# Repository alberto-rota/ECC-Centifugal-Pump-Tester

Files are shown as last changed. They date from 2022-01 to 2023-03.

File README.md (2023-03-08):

# ECC Centrifugal pump compliancy tester
An IR-based device for testing the compliance of ECC centrifugal pumps in terms of the hemolitic/thrombogenic effects of the magnetic impeller unstable rotations. 
Employs an LSTM classifier to distinguish proximity signals from compliant and non-compliant pumps.

_This project is in collaboration with Qura s.r.l._

***
* Active Contributors: **Alberto Rota**, Nicolò Pasini, Silvia Bonomi, Gaia Albani, Elisabetta Criseo
***

## Interface Installation
* Windows: *Link not yet Available* 
* Linux: *Link not yet Available*
You should contact the maintaining developer to have the links)

**NOTE:** The interface embeds the ML kodel for the compliancy classification, hence at the moment it includes the whole TensorFlow framework. The size of the download is close to 1GB, but will be optimized in the future

**Requirements:** No requirement is necessary. The program runs as a standalone application.

After downloading, copy the folder in the directory of your choice. To run the interface excecute the file `qura_pump_tester`, which opens the following window

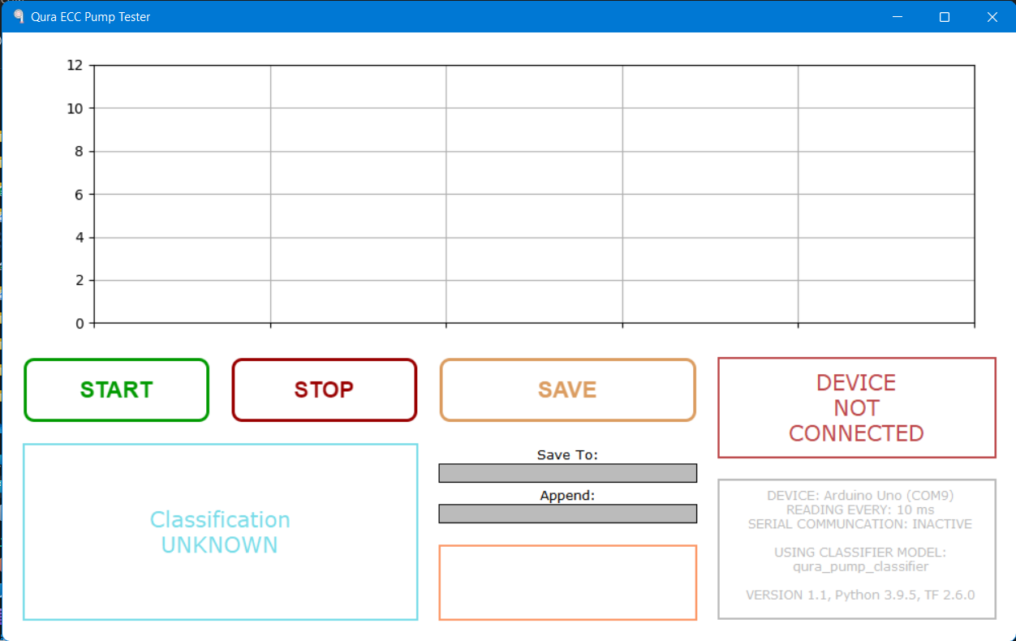
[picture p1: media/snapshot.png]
snap


***
## How to use this Interface
After being plugged in, the device should be detected automatically in the top-right frame, which becomes green and displays the device name, COM-Port and Baudrate. If the Serial Communication is not initialized correctly, the bottom-right gray frame shows `SERIAL COMMUNICATION: INACTIVE`: check that the device name in the `config` file is correct.
With serial communication estabilished, the workflow to be followed is:
* Press the green **START** button to start recording the signals. Ideally, the **START** button should be pressed when the pump is steadily rotating at 500 rpm. The recordings will be displayed in the cart area in real time
* Press the red **STOP** button to stop the recording. Ideally, the **STOP** button should be pressed when the pump is still rotating at 500 rpm and before stopping the driver motion. After this button is pressed, the AI model performs the classification and displays the output in the bottom-left frame
* Press the orange **SAVE** button to save the recording for the last pump tested on a *.csv* file. The file will be saved in the folder specified in the "Save to:" textbox; if any text is specified in the "Append:" textbox, that same text will be appended to the filename. For example, with:
  - *Save to:* C:\Users\qura\tests
  - *Append:* appended

The file will be saved as:
`C:\Users\qura\tests\DDMMYY_HHMMSS_appended.csv` [DayMonthYear_HourMinutesSeconds]

***

## Project Overview
The device is placed on top of the pump while it is mounted and rotating on the driver. The entity of the fluttering is measured as the distance from the 6 IR phototransistors (OPB730F) placed on the pump roof facing downward. The bell-shaped sensitivity curve of the OPB730F ([see datasheet](https://github.com/alberto-rota/Qura-ECC-Centifugal-Pump-Tester/tree/main/media/OPB730F%20Datasheet.pdf)) suggest an inverse relationship between distance and output voltage. The signals are then aquired by an ESP32 and sent to a computer in serial communication

The acquisition circuit is reported below:

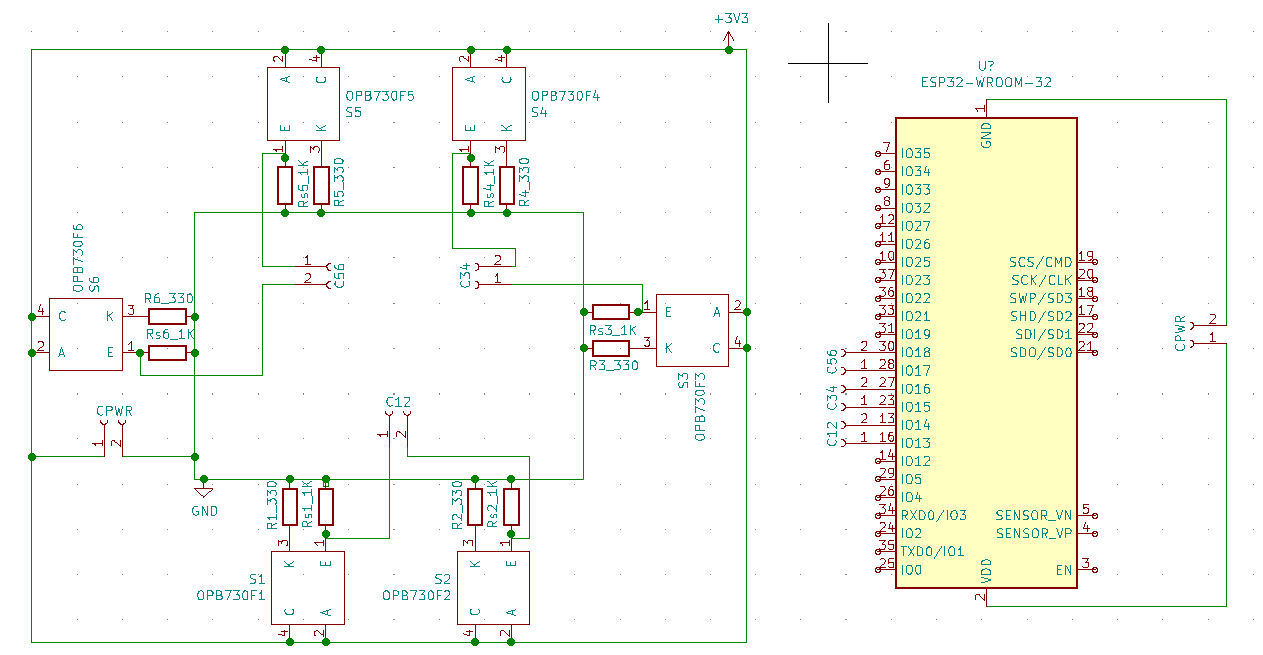
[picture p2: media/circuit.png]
circuit


and it has been embedded in a custom-made PCB, which connects to the ESP32 via JST connectors.
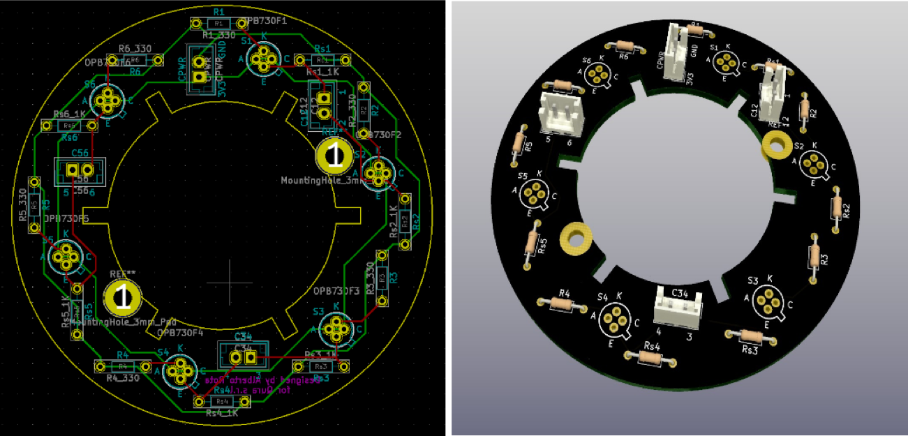
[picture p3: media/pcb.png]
pcb


## Compliancy assessment
Since no evitent distinction critheria emerge from the acquired signals, an AI-based classifier has been trained by recording the signals from 51 pumps at low (100 rpm) and high (500 rpm) speed.
The model is based on a LSTM architecture. The signal is divided in 75-samples-long windows, sliced from the signals (which may have different length) with a padding of 25. No data-augmentation is performed. After an 8-fold cross validation, the model from the best fold classified a test set with an **accuracy of 88%**. 

*The LSTM model is being developed further, no additonal details on the results are therefore provided*

## Prototype Design 
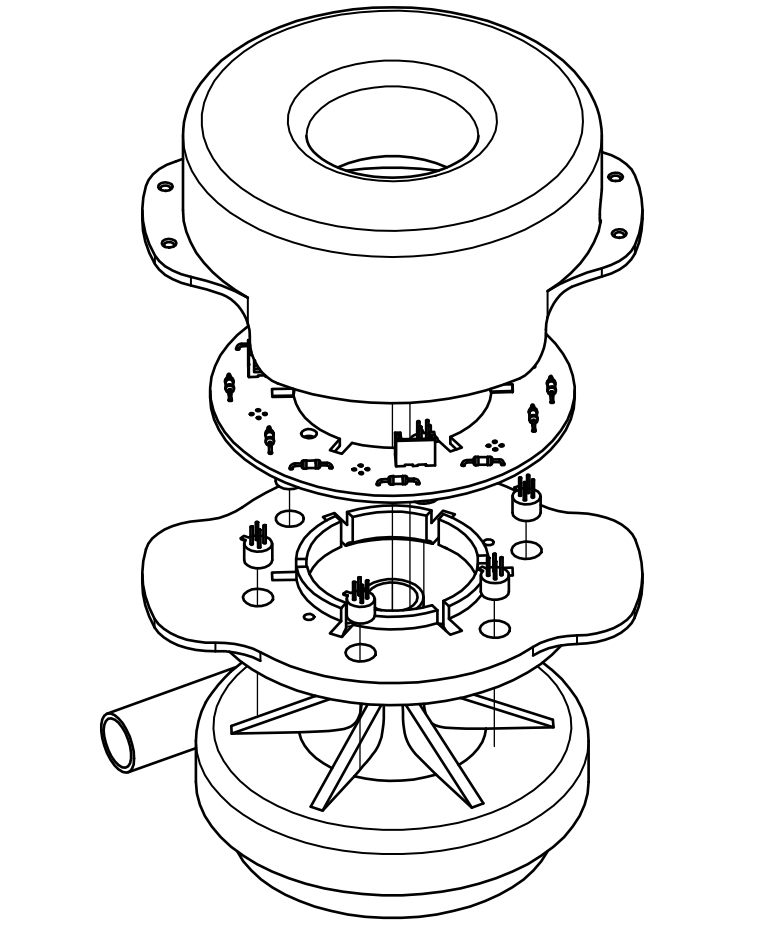
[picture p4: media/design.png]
design


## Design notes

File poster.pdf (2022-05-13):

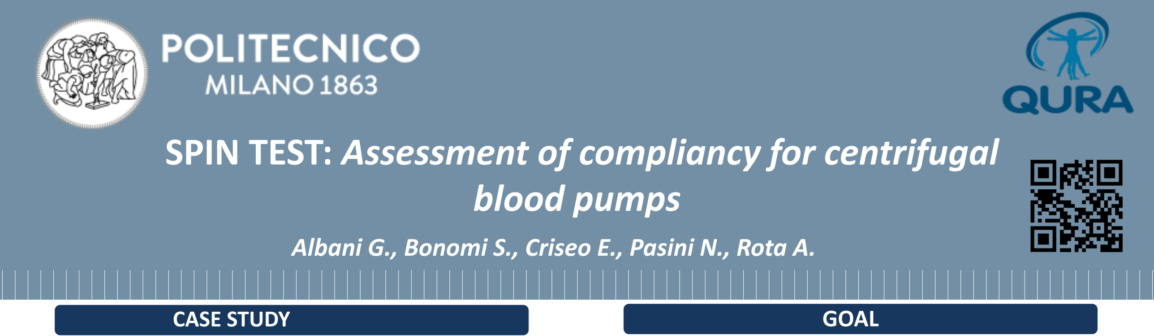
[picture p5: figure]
blood pumps; CASE STUDY; GOAL

# SPIN TEST: Assessment of compliancy for centrifugal

Centrifugal Blood Pumps: devices used during extracorporeal circulation; the blood flow enters from the inlet of the pump and is pushed by the rotor in such a way as to exit through the outlet, oriented at an angle of 90 ° to the inlet

Company
operator

Hearing the
noise produced
by the pump

Motion of
pump’s
impeller

Classify the pumps
in compliant and
not compliant

Find a STANDARDIZED, AUTOMATED and NON-DAMAGING protocol to test the pump in order to assess its acceptability

1. Optimize the process
2. Standardize the modality to eliminate the intra-subject variability
3. Not distructive test
4. Reproducible
5. Not invasive approach

## MATHERIALS AND METHODS

## RESULTS AND DISCUSSION

Efficacy: measure how much the impeller approaches or moves away from the sensors

OPB730F sensors

✓Linearity range [2.5-10mm] ✓Filter
✓Internal barrier
✓Max Input diode’s current = 50 mA ✓R diode > 36Ω

Infrared
LED | Transistor

MODEL IDEA

1, S≥0.5 ⇒ Compliant
0, S<0.5 ⇒ Non Compliant

C=

K=2⋅|S−0.5|⋅100

The classifier works applying a simply threshold:

The confidence of the classificator is given by:

Initial dataset is composed by 33 pumps:
- 11 pumps are used to calculate the the accuracy of the model
- 22 pumps are used for the training phase

Problem: movement of the impeller which tends to make a flickering movement along the z-x and z-y plane. This could cause haemolysis and thrombi

z

Solution: Spin Test to quantify the flickering of the impeller and classify the pumps between compliant and non-compliant

Today’s
approach

THE DATASET

Test on-site at Qura s.r.l. to validate our model: 13 pumps tested not included in the training dataset

Initial Results
29 pumps | Properly classified
4 pumps | False negative
Accuracy | 0.88

Results
11 pumps | Properly classified
2 pumps | False negative
Accuracy | 0.84

### VALIDATION TEST

The results
confirm the
validity of the
model

Explanation: when a voltage is applied, the diode emits IR light that propagates until hits an object and it is reflected towards the sensor

Every sensor used
is associated to a
circuit

PCB (Printed Circuit Board): 6 sensors were used to achieve a precise measure of the impeller fluttering.
The PCB reduces the extension of the circuits and makes the set-up compact. The PCB is then fixed to the pump through a support which allows maintaining the sensors in the right position

Development Board: the development board is what brings the output signals of the sensors as input for the graphical interface. In this way the signals are displayed to the operator in a clear way

Data Acquisition: the set-up with is used to register the signal from 51 pumps. These were divided a priori between compliant and non compliant.

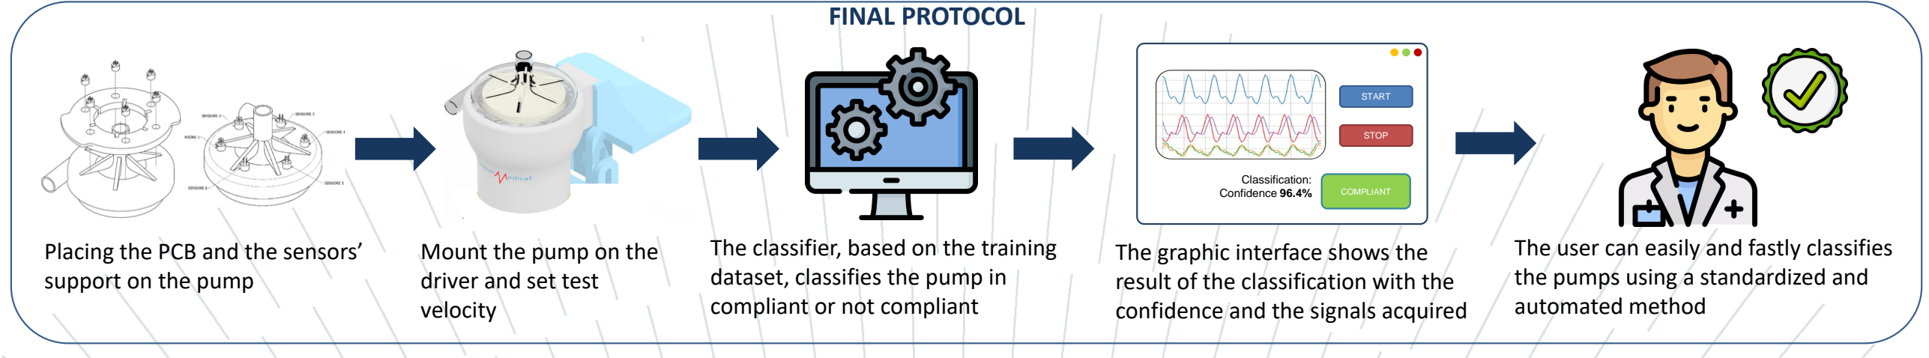
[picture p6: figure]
START; STOP; COMPLIANT; Classification: Confidence 96.4%; FINAL PROTOCOL; Placing the PCB and the sensors’ support on the pump; Mount the pump on the driver and set test velocity; The classifier, based on the training dataset, classifies the pump in compliant or not compliant; The graphic interface shows the result of the classification with the confidence and the signals acquired; the pumps using a standardized and automated method

The user can easily and fastly classifies

Impact: this would mean increasing the efficiency of the the process in terms of time and human resources

New approach:

OPTICAL PROXIMITY SENSORS | PCB AND DEVELOPMENT BOARD | MACHINE LEARNING

the operator no longer has a determining role in the classification of the pumps. In fact, through a machine learning model, the classification becomes more objective

CNN Model Implementation

1. The raw data obtained from the sensors is elaborated using data augmentation, in this way it is obtained the training set
2. Preparation of test-set
3. Definition of model architecture

Model Tuning: defining optimal parameters to get the best result with the model architecture chosen. The parameters to be optimized are: dimension of the windows used to elaborate the data, filters’ dimension and their number

Data acquisition was performed using two kinds of test: imposing a rotation of 100 rpm or 500 rpm, both times for 5 seconds

Albani G., Bonomi S., Criseo E., Pasini N., Rota A.

Classification

Expected Result

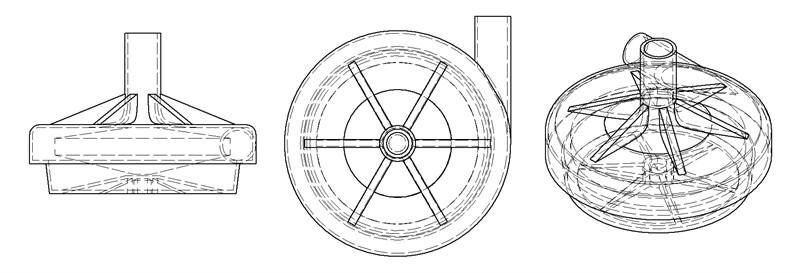
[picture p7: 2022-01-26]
media/eccpump.png

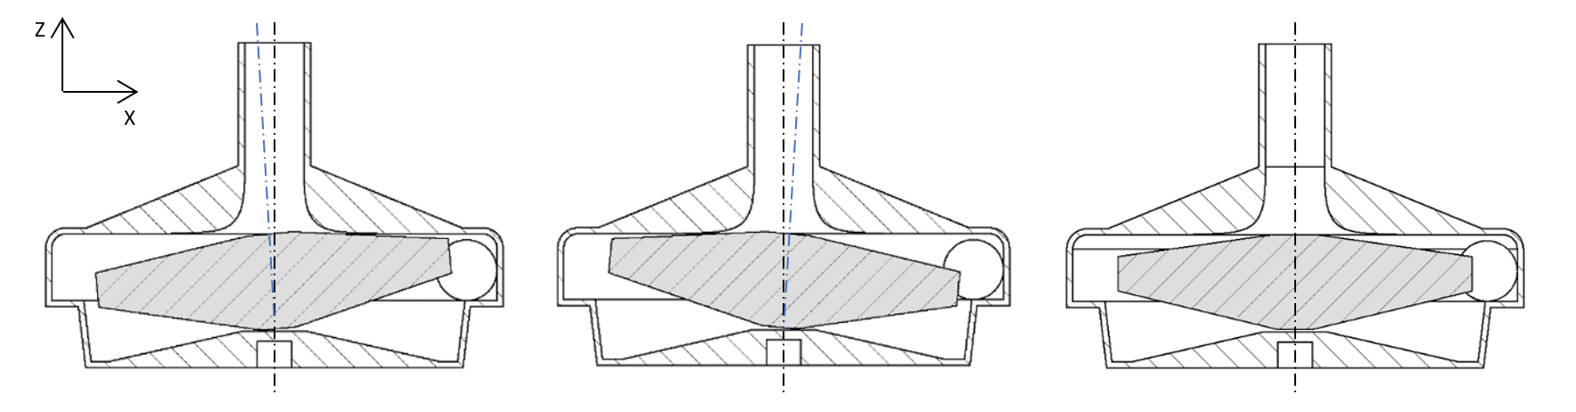
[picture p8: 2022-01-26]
media/fluttering.png

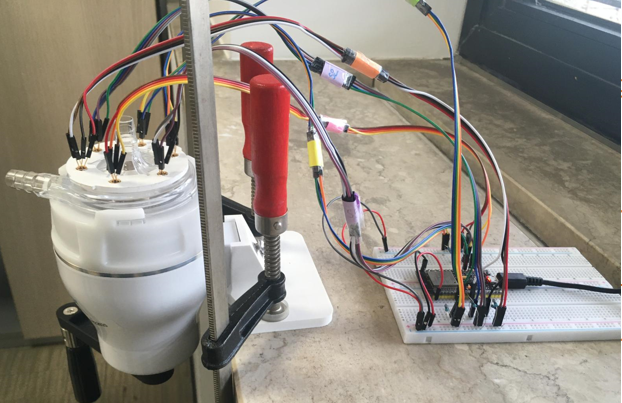
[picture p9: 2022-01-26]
media/prototype.png

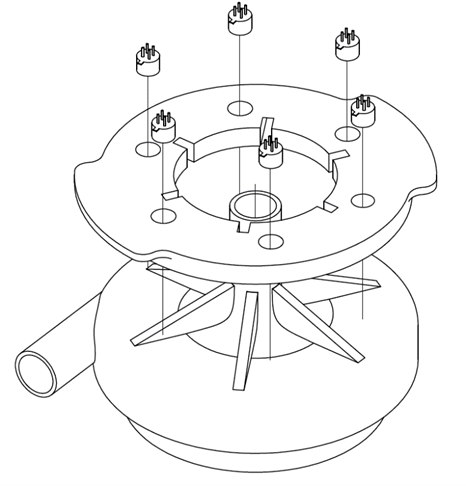
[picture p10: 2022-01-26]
media/sensorpositioning.png

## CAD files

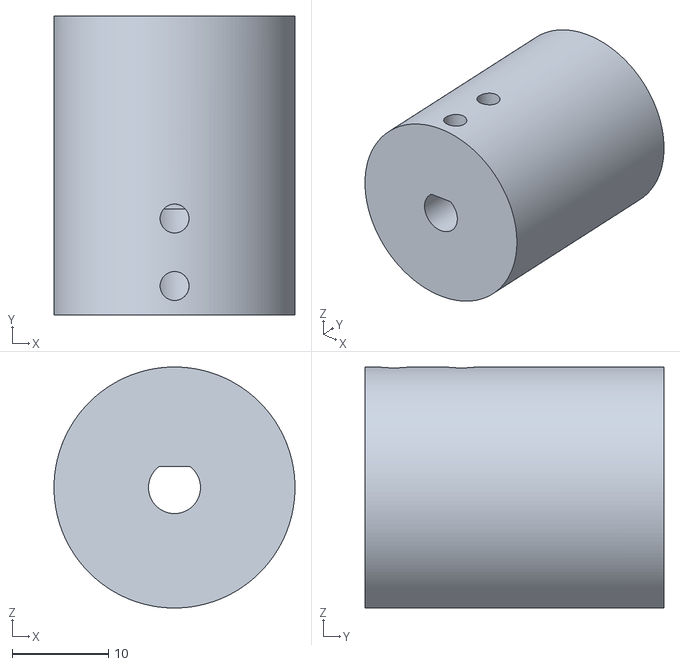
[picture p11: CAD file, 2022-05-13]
design/MotorDriverCoupler.stl
25.0 x 31.0 x 25.0

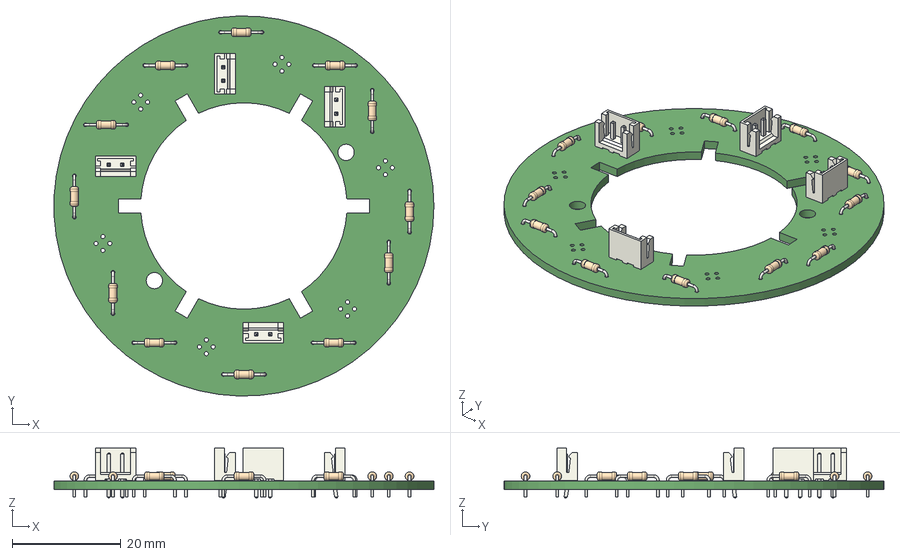
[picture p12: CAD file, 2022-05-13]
pcb/qura_pump_pcb_model.step
70.0 x 70.0 x 9.20 mm

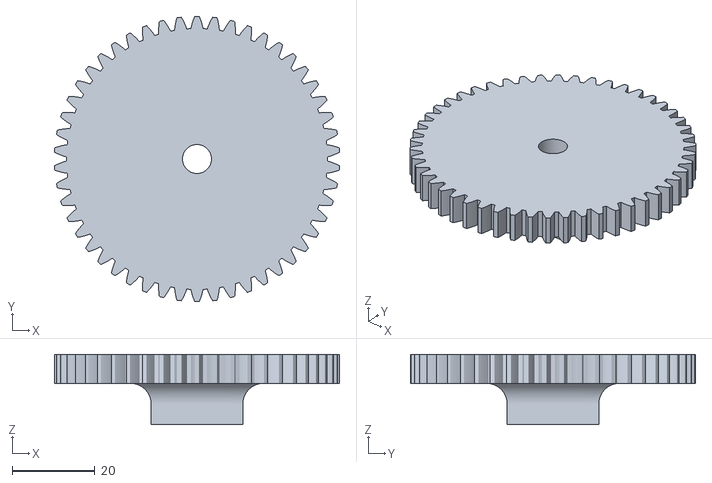
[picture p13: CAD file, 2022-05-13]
design/BigGear.stl
68.9 x 69.0 x 17.0

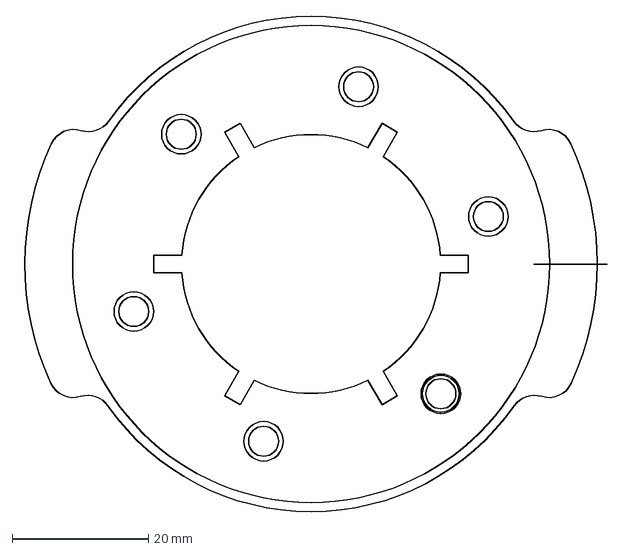
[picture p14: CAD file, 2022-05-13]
pcb/pcb_footprint.dxf
86.7 x 72.7 mm

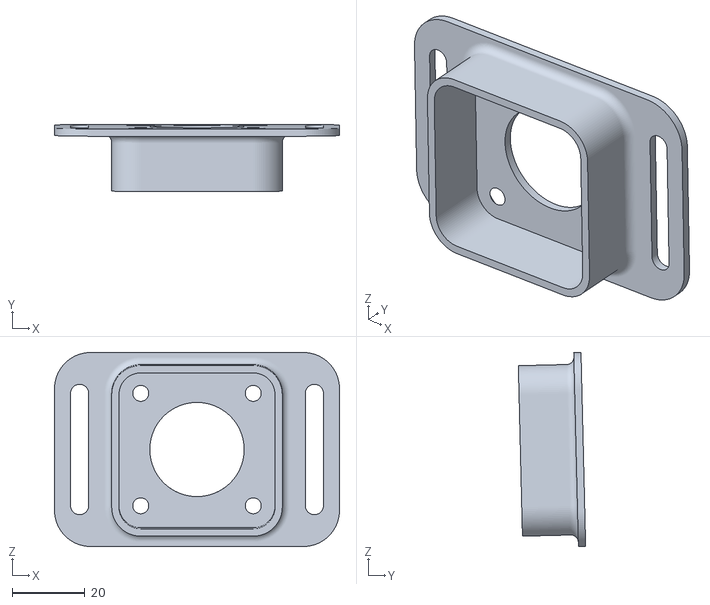
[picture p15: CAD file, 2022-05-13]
design/Slider.stl
78.5 x 18.6 x 53.5

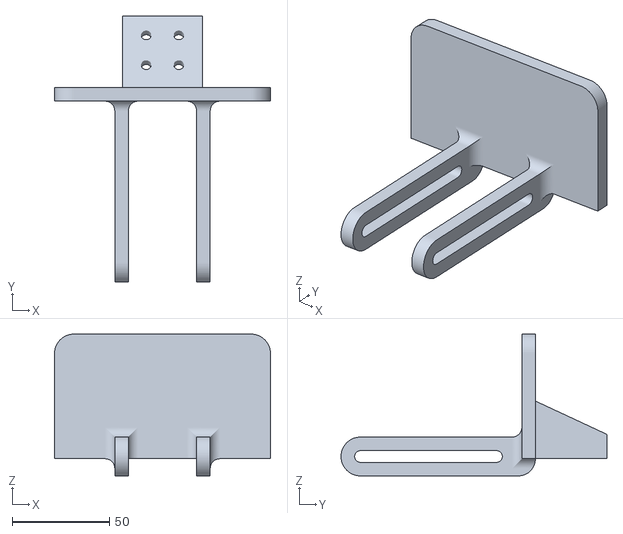
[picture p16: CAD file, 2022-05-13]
design/driver_lock.stl
111.1 x 136.8 x 73.0

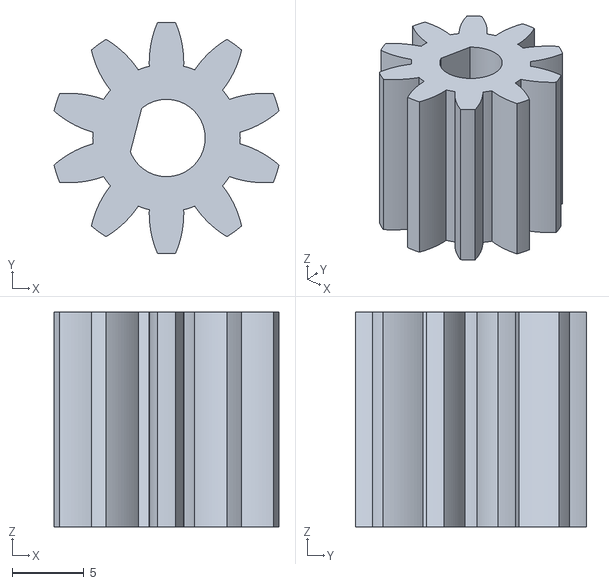
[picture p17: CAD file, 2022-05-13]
design/SmallGear.stl
15.7 x 16.2 x 15.0

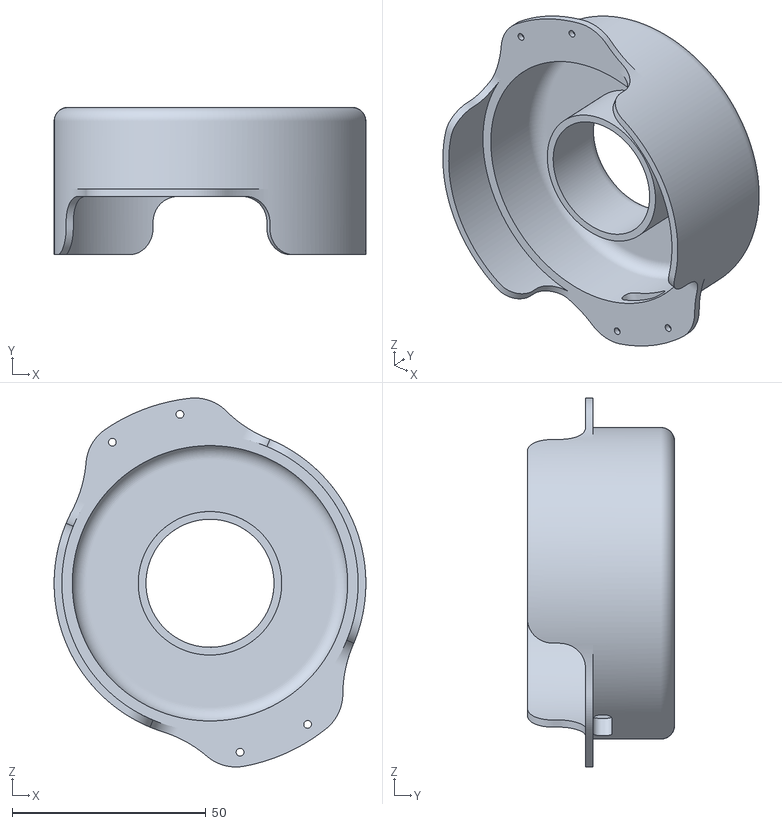
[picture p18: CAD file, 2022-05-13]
design/Case.stl
80.4 x 38.0 x 95.2

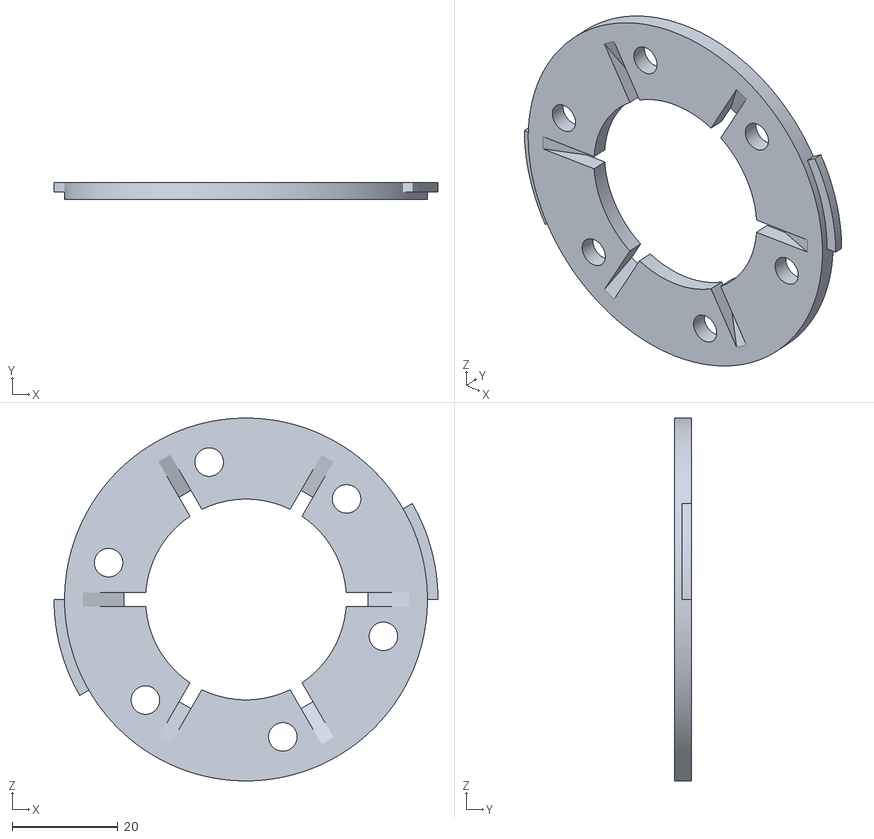
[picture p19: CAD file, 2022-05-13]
design/sensor_housing_v3.stl
72.7 x 3.20 x 68.7

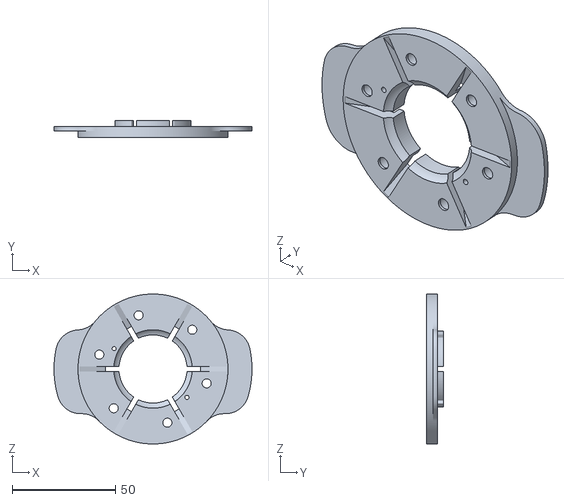
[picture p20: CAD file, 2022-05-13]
design/Housing.stl
96.0 x 8.20 x 72.7

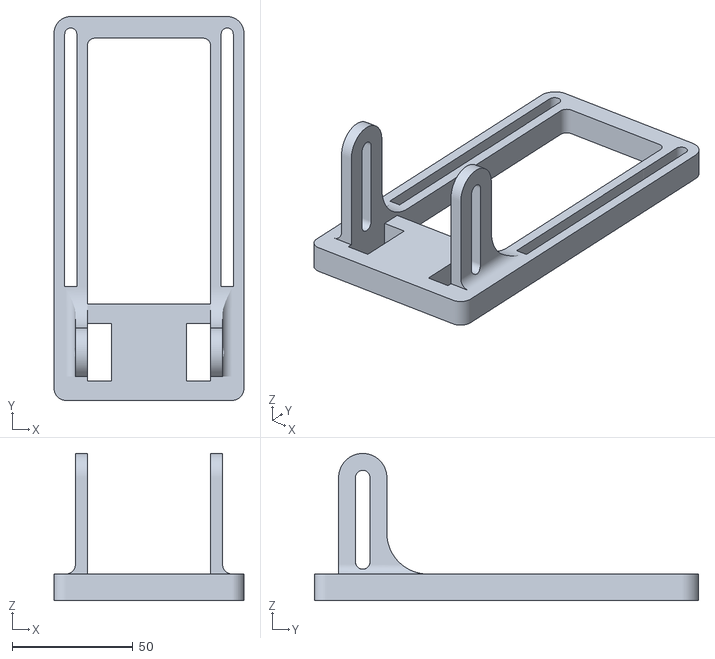
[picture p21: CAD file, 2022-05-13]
design/VSlider.stl
78.7 x 159.2 x 61.0

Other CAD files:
design/Assembly-1.dwg
design/Pump_drawing.dwg
design/OldVersions/Pump_drawing.0001.dwg
design/Assembly.iam
design/Assembly/Design Accelerator/Spur Gear11.ipt
design/Assembly/Design Accelerator/Spur Gear12.ipt
design/Assembly/Design Accelerator/Spur Gear13.ipt
design/Assembly/Design Accelerator/Spur Gear21.ipt
design/Assembly/Design Accelerator/Spur Gear22.ipt
design/Assembly/Design Accelerator/Spur Gears1.iam
design/Assembly/Design Accelerator/Spur Gears2.iam
design/Assembly1.iam
design/Case.ipt
design/Driver.ipt
design/DriverMount.iam
design/Driver_lock.ipt
design/Frame.ipt
design/Housing.ipt
design/Impeller.ipt
design/Motor-Driver Coupler.ipt
design/OldVersions/Assembly.0049.iam
design/OldVersions/Case.0003.ipt
design/OldVersions/Complete.0004.iam
design/OldVersions/Driver.0008.ipt
design/OldVersions/DriverMount.0004.iam
design/OldVersions/Driver_lock.0015.ipt
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

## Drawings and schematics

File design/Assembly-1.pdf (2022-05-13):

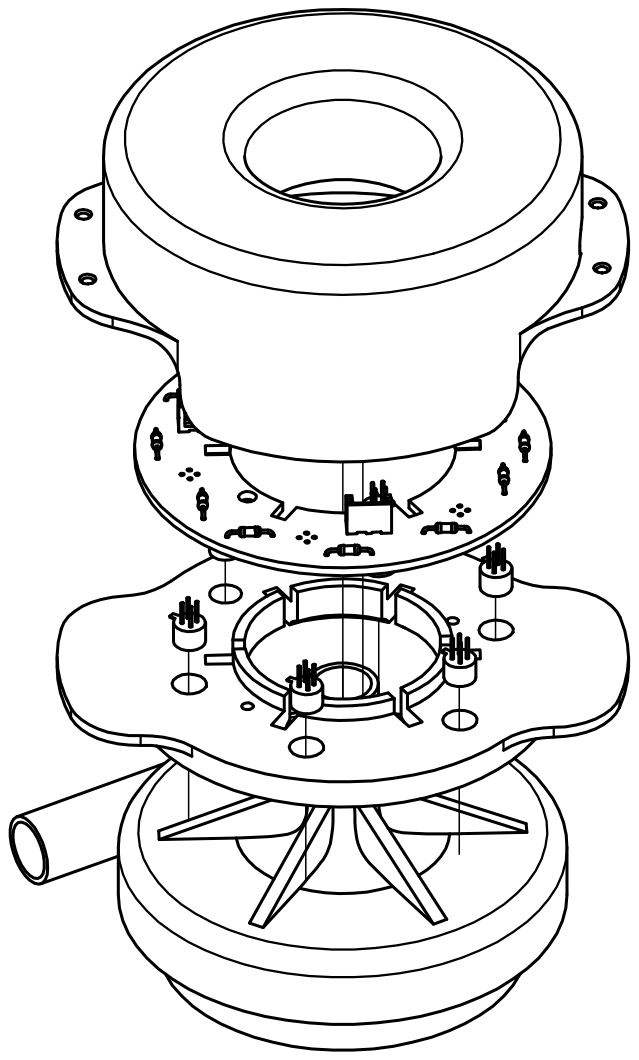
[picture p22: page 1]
Designed by; Checked by; Approved by; Date

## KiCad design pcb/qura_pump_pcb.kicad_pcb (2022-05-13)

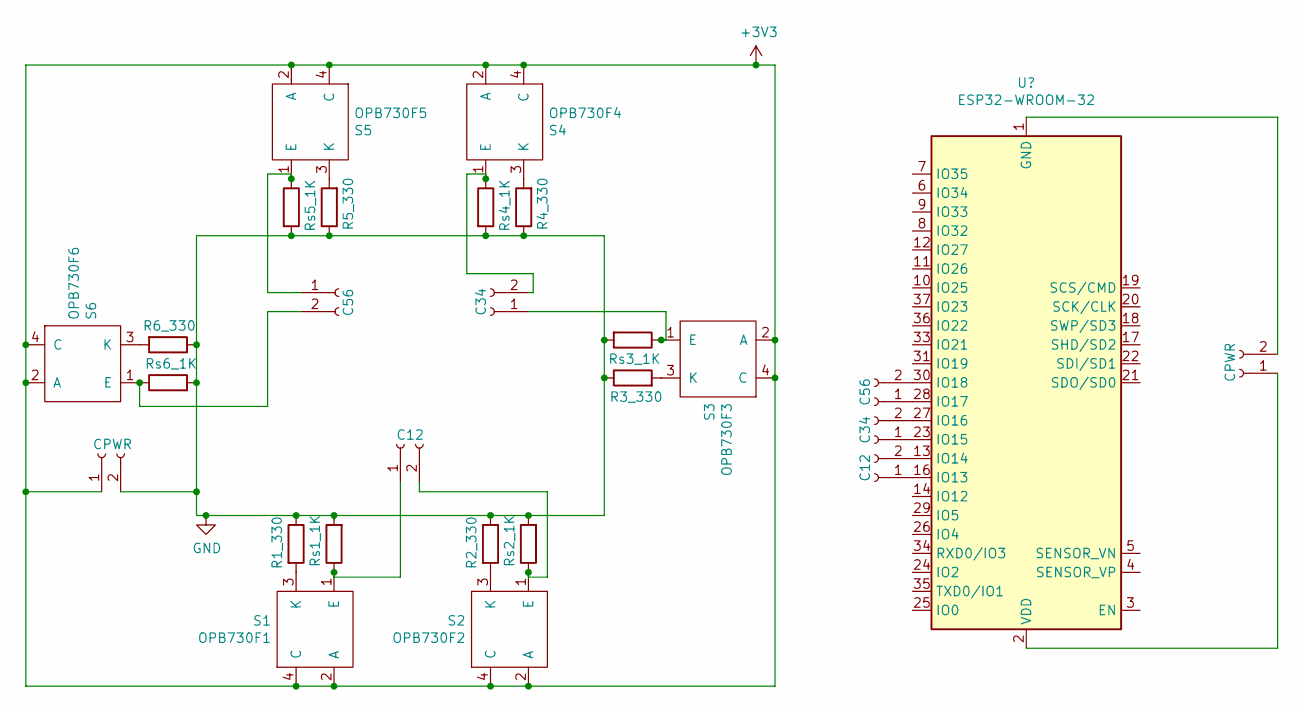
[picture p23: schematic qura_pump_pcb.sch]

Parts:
C12: C12; JST_EH_B2B-EH-A_1x02_P2.50mm_Vertical
C34: C34; JST_EH_B2B-EH-A_1x02_P2.50mm_Vertical
C56: C56; JST_EH_B2B-EH-A_1x02_P2.50mm_Vertical
CPWR1: CPWR; JST_EH_B2B-EH-A_1x02_P2.50mm_Vertical
OPB730F1: S1; OPB730F
OPB730F2: S2; OPB730F
OPB730F3: S3; OPB730F
OPB730F4: S4; OPB730F
OPB730F5: S5; OPB730F
OPB730F6: S6; OPB730F
R1: R1_330; R_Axial_DIN0204_L3.6mm_D1.6mm_P7.62mm_Horizontal
R2: R2_330; R_Axial_DIN0204_L3.6mm_D1.6mm_P7.62mm_Horizontal
R3: R3_330; R_Axial_DIN0204_L3.6mm_D1.6mm_P7.62mm_Horizontal
R4: R4_330; R_Axial_DIN0204_L3.6mm_D1.6mm_P7.62mm_Horizontal
R5: R5_330; R_Axial_DIN0204_L3.6mm_D1.6mm_P7.62mm_Horizontal
R6: R6_330; R_Axial_DIN0204_L3.6mm_D1.6mm_P7.62mm_Horizontal
Rs1: Rs1_1K; R_Axial_DIN0204_L3.6mm_D1.6mm_P7.62mm_Horizontal
Rs2: Rs2_1K; R_Axial_DIN0204_L3.6mm_D1.6mm_P7.62mm_Horizontal
Rs3: Rs3_1K; R_Axial_DIN0204_L3.6mm_D1.6mm_P7.62mm_Horizontal
Rs4: Rs4_1K; R_Axial_DIN0204_L3.6mm_D1.6mm_P7.62mm_Horizontal
Rs5: Rs5_1K; R_Axial_DIN0204_L3.6mm_D1.6mm_P7.62mm_Horizontal
Rs6: Rs6_1K; R_Axial_DIN0204_L3.6mm_D1.6mm_P7.62mm_Horizontal

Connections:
+3V3: CPWR1.1, OPB730F1.2 (A), OPB730F1.4 (C), OPB730F2.2 (A), OPB730F2.4 (C), OPB730F3.2 (A), OPB730F3.4 (C), OPB730F4.2 (A), OPB730F4.4 (C), OPB730F5.2 (A), OPB730F5.4 (C), OPB730F6.2 (A), OPB730F6.4 (C); also elsewhere on the board
GND: CPWR1.2, R1.1, R2.1, R3.1, R4.1, R5.1, R6.1, Rs1.2, Rs2.2, Rs3.2, Rs4.2, Rs5.2, Rs6.2; also elsewhere on the board
unnamed: C12.1, OPB730F1.1 (E), Rs1.1
unnamed: C12.2, OPB730F2.1 (E), Rs2.1
unnamed: C34.1, OPB730F3.1 (E), Rs3.1
unnamed: C34.2, OPB730F4.1 (E), Rs4.1
unnamed: C56.1, OPB730F5.1 (E), Rs5.1
unnamed: C56.2, OPB730F6.1 (E), Rs6.1
unnamed: OPB730F1.3 (K), R1.2
unnamed: OPB730F2.3 (K), R2.2
unnamed: OPB730F3.3 (K), R3.2
unnamed: OPB730F4.3 (K), R4.2
unnamed: OPB730F5.3 (K), R5.2
unnamed: OPB730F6.3 (K), R6.2

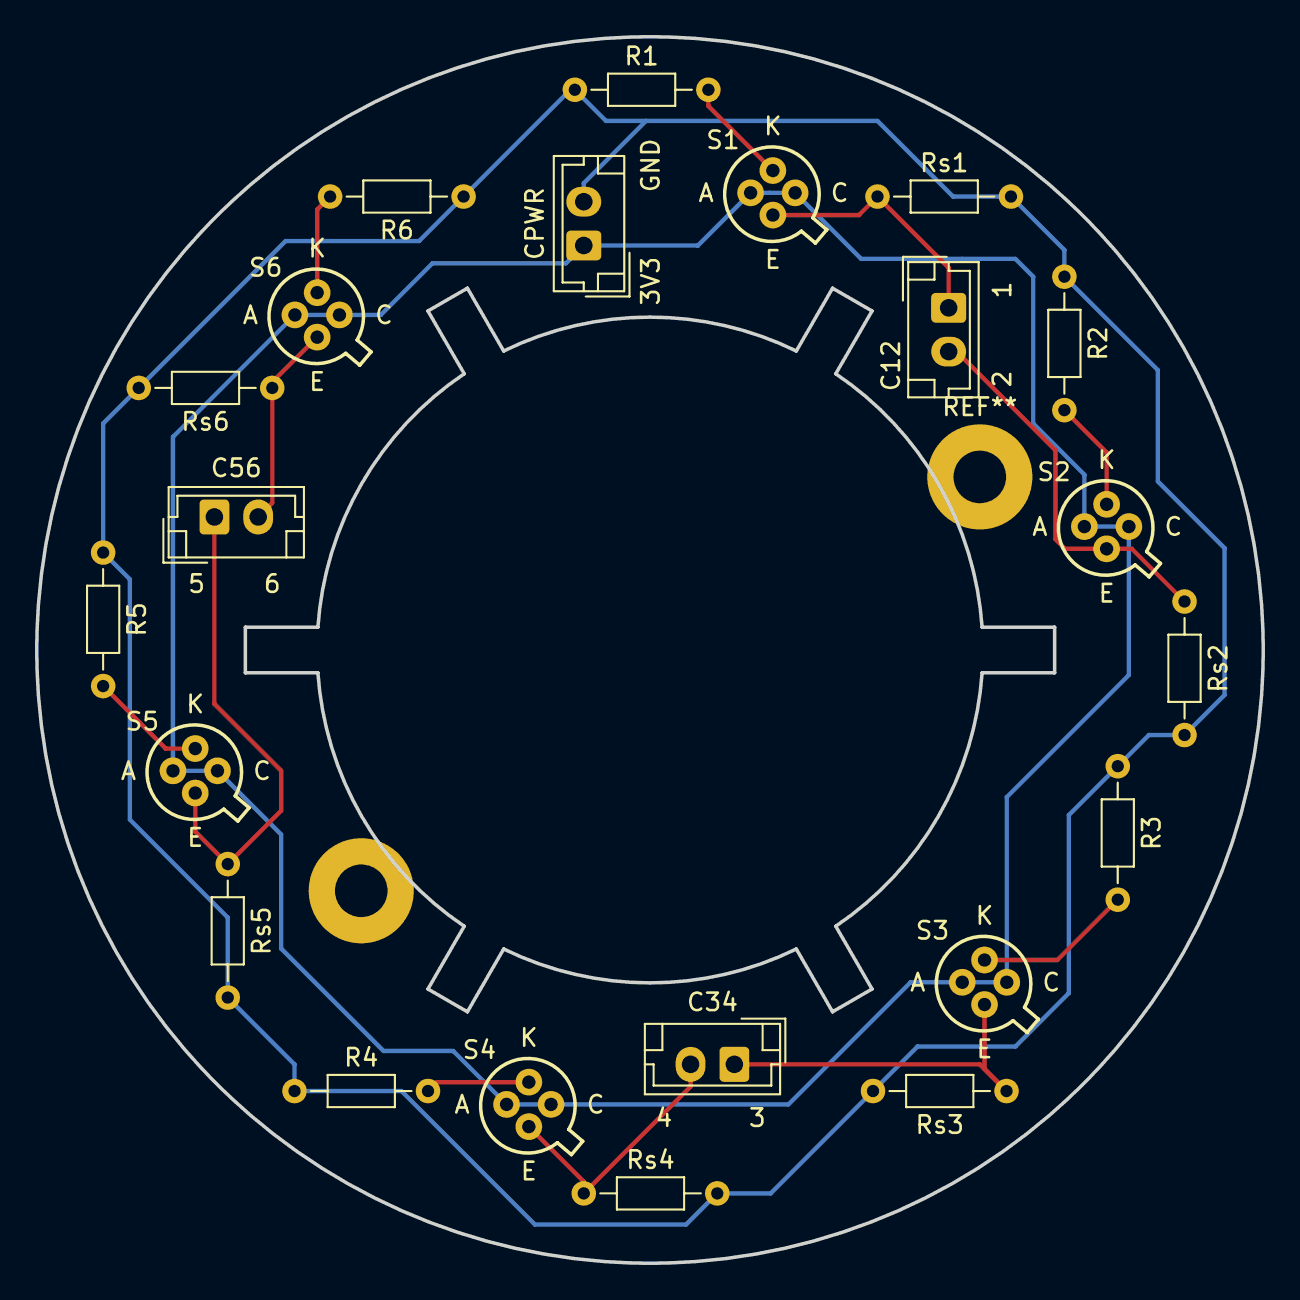
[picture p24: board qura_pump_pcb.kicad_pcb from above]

Board: 2 copper layers, 70.0 x 70.0 mm, 22 parts (0 on the bottom side), 14 nets.

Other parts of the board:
CPWR: CPWR; JST_EH_B2B-EH-A_1x02_P2.50mm_Vertical

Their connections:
+3V3: CPWR.1; also elsewhere on the board
GND: CPWR.2; also elsewhere on the board

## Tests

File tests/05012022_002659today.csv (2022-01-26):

8.699999999999999956e-01 | 3.259999999999999787e+00 | 5.509999999999999787e+00 | 7.889999999999999680e+00 | 9.759999999999999787e+00 | 1.000000000000000000e+01
8.399999999999999689e-01 | 3.330000000000000071e+00 | 5.620000000000000107e+00 | 7.980000000000000426e+00 | 9.310000000000000497e+00 | 1.053999999999999915e+01
8.000000000000000444e-01 | 3.390000000000000124e+00 | 5.719999999999999751e+00 | 8.000000000000000000e+00 | 8.789999999999999147e+00 | 1.155000000000000071e+01
7.700000000000000178e-01 | 3.450000000000000178e+00 | 5.799999999999999822e+00 | 7.940000000000000391e+00 | 8.320000000000000284e+00 | 1.200000000000000000e+01
7.399999999999999911e-01 | 3.509999999999999787e+00 | 5.870000000000000107e+00 | 7.830000000000000071e+00 | 8.039999999999999147e+00 | 1.141000000000000014e+01
7.099999999999999645e-01 | 3.560000000000000053e+00 | 5.929999999999999716e+00 | 7.650000000000000355e+00 | 8.029999999999999361e+00 | 1.038000000000000078e+01
6.700000000000000400e-01 | 3.620000000000000107e+00 | 5.969999999999999751e+00 | 7.429999999999999716e+00 | 8.279999999999999361e+00 | 1.000999999999999979e+01
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

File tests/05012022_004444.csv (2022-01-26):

1.860000000000000098e+00 | 3.870000000000000107e+00 | 4.139999999999999680e+00 | 7.870000000000000107e+00 | 8.089999999999999858e+00 | 1.165000000000000036e+01
1.879999999999999893e+00 | 3.839999999999999858e+00 | 4.080000000000000071e+00 | 7.700000000000000178e+00 | 8.000000000000000000e+00 | 1.065000000000000036e+01
1.889999999999999902e+00 | 3.799999999999999822e+00 | 4.040000000000000036e+00 | 7.490000000000000213e+00 | 8.199999999999999289e+00 | 1.000999999999999979e+01
1.909999999999999920e+00 | 3.759999999999999787e+00 | 4.009999999999999787e+00 | 7.250000000000000000e+00 | 8.609999999999999432e+00 | 1.040000000000000036e+01
1.919999999999999929e+00 | 3.709999999999999964e+00 | 4.000000000000000000e+00 | 6.980000000000000426e+00 | 9.130000000000000782e+00 | 1.140000000000000036e+01
1.939999999999999947e+00 | 3.660000000000000142e+00 | 4.009999999999999787e+00 | 6.719999999999999751e+00 | 9.609999999999999432e+00 | 1.199000000000000021e+01
1.949999999999999956e+00 | 3.609999999999999876e+00 | 4.030000000000000249e+00 | 6.480000000000000426e+00 | 9.929999999999999716e+00 | 1.155000000000000071e+01
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

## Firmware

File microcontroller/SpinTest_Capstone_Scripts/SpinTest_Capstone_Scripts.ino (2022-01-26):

int SENS_1_PIN = 27;
int SENS_3_PIN = 32;
int SENS_2_PIN = 33;
int SENS_5_PIN = 2;
int SENS_4_PIN = 4;
int SENS_6_PIN = 15;
int DELAY = 10;


void setup() {

  pinMode(SENS_1_PIN, INPUT);
  pinMode(SENS_3_PIN, INPUT);
  pinMode(SENS_2_PIN, INPUT);
  pinMode(SENS_5_PIN, INPUT);
  pinMode(SENS_4_PIN, INPUT);
  pinMode(SENS_6_PIN, INPUT);


  Serial.begin(9600);
}

void loop() {
 
  int sensed1=analogRead(SENS_1_PIN);
  sensed1=map(sensed1,0,4095,0,3300);

  int sensed2=analogRead(SENS_2_PIN);
  sensed2=map(sensed2,0,4095,0,3300);
  
  int sensed3=analogRead(SENS_3_PIN);
  sensed3=map(sensed3,0,4095,0,3300);
  
  int sensed4=analogRead(SENS_4_PIN);
  sensed4=map(sensed4,0,4095,0,3300);

  int sensed5=analogRead(SENS_5_PIN);
  sensed5=map(sensed5,0,4095,0,3300);

  int sensed6=analogRead(SENS_6_PIN);
  sensed6=map(sensed6,0,4095,0,3300);
  
  Serial.print(sensed1);
  Serial.print(",");
  Serial.print(sensed2);
  Serial.print(",");
  Serial.print(sensed3);
  Serial.print(",");
  Serial.print(sensed4);
  Serial.print(",");
  Serial.print(sensed5);
  Serial.print(",");
  Serial.print(sensed6);
  Serial.println();

  delay(DELAY);
}
